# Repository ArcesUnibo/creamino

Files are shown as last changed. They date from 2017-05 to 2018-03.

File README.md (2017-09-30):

# creamino
Open-source Framework for Fast Developmnt of EEG-based BCI Systems

Download and Install git-for-windows.github.io from https://git-for-windows.github.io
Download and Install TortoiseGit from https://github.com/ArcesUnibo/creamino

To obtain creamino we would do the following:

Create a folder that will hold the Git project
example: c:\work
Selecting this folder, right click on it and use the command: Git Clone...
In the dialog we provide:
The URL of the project http://github.com/ArcesUnibo/creamino
The directory of the project. This will be automatically populated with the name of the project in our selected folder.
Select the Recursive checkbox.

Thank you for using Creamino!

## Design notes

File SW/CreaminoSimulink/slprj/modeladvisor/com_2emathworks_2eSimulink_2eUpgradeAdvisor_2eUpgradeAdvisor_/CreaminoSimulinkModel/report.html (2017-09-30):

Model Advisor Report
Simulink version: 8.4 | Model version: 1.3
System: CreaminoSimulinkModel | Current run: 10-Feb-2016 17:30:59

#### No results to display. Select one or more items in the left pane, then press Run Selected Checks.

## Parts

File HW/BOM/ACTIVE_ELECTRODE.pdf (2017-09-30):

Description | Designator | Footprint | Comment
Capacitor (Surface Mount) CP1 | CC3225-1210 220u
Capacitor (Surface Mount) CP2 | CC1005-0402 22n
Default Diode | D1 | SC79 | 1N4148
Semiconductor Resistor | R1 | CR1005-0402 1.6K
Semiconductor Resistor | R2 | CR1608-0603 71.4K
Semiconductor Resistor | R3 | CR1005-0402 604K
Semiconductor Resistor | R4 | CR1005-0402 33K
OPA378AIDBVT | U1 | SOT23-5DVB | OPA378AIDBVT

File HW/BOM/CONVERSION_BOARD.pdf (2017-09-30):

Description | Designator Footprint | Comment
ADP122-3.3 | A1 | UJ-5
ADP122-3.3 | A3 | UJ-5
ADS1298 | ADC1 | PAG64
Polarized Capacitor (Surface Mount) | CP1 | CC2012-0805 10u
Capacitor (Semiconductor SIM Model) | CP2 | CC1005-0402 100n
Capacitor (Semiconductor SIM Model) | CP3 | CC1005-0402 100n
Capacitor (Semiconductor SIM Model) | CP6 | CC1005-0402 470n
Capacitor (Semiconductor SIM Model) | CP17 | CC1005-0402 1u
Capacitor (Semiconductor SIM Model) | CP18 | CC1005-0402 1u
Capacitor (Semiconductor SIM Model) | CP25 | CC1005-0402 100n
Capacitor (Semiconductor SIM Model) | CP26 | CC1005-0402 1u
Capacitor (Semiconductor SIM Model) | CP27 | CC1005-0402 100n
Capacitor (Semiconductor SIM Model) | CP28 | CC1005-0402 1u
Capacitor (Semiconductor SIM Model) | CP29 | CC1005-0402 470n
Capacitor (Semiconductor SIM Model) | CP30 | CC1005-0402 470n
Capacitor (Semiconductor SIM Model) | CP31 | CC1005-0402 470n
Capacitor (Semiconductor SIM Model) | CP32 | CC1005-0402 470n
Capacitor (Semiconductor SIM Model) | CP33 | CC1005-0402 470n
Capacitor (Semiconductor SIM Model) | CP34 | CC1005-0402 470n
Capacitor (Semiconductor SIM Model) | CP35 | CC1005-0402 470n
Capacitor (Semiconductor SIM Model) | CP36 | CC1005-0402 470n
Polarized Capacitor (Surface Mount) | CP37 | CC1608-0603 22uF
Capacitor (Semiconductor SIM Model) | CP38 | CC1005-0402 1u
Capacitor (Semiconductor SIM Model) | CP39 | CC1005-0402 1u
Capacitor (Semiconductor SIM Model) | CP40 | CC1005-0402 100n
Capacitor (Semiconductor SIM Model) | CP41 | CC1005-0402 1u
Capacitor (Semiconductor SIM Model) | CP42 | CC1005-0402 100p
Polarized Capacitor (Surface Mount) | CP43 | CC2012-0805 10uF
Capacitor (Semiconductor SIM Model) | CP44 | CC1005-0402 100n
Capacitor (Semiconductor SIM Model) | CP45 | CC1005-0402 100n
Polarized Capacitor (Surface Mount) | CP46 | CC2012-0805 10u
Capacitor (Semiconductor SIM Model) | CP47 | CC1005-0402 100n
Polarized Capacitor (Surface Mount) | CP48 | CC2012-0805 10u
Capacitor (Semiconductor SIM Model) | CP49 | CC1005-0402 100n
Polarized Capacitor (Surface Mount) | CP50 | CC2012-0805 10u
Capacitor (Semiconductor SIM Model) | CP51 | CC1005-0402 100n
Capacitor (Semiconductor SIM Model) | CP51_TANTCC3216-1206 1u
Polarized Capacitor (Surface Mount) | CP52 | CC2012-0805 10u
Capacitor (Semiconductor SIM Model) | CP55 | CC1005-0402 1u
Capacitor (Semiconductor SIM Model) | CP56 | CC1005-0402 1u
Header, 3-Pin | JPV | HDR1X3 | JPV
ADuM2401 | O1A | RW-16
ADuM2401 | O1B | RW-16
ADUM6000 | O2 | RW-16
Header, 10-Pin, Dual row | P1 | HDR2X10 | Header 10X2
Header, 8-Pin | P3 | HDR1X8 | Dx UP
Header, 8-Pin | P4 | HDR1X8 | Dx DOWN
Header, 8-Pin | P5 | HDR1X8 | Sx UP

Header, 6-Pin | P6 | HDR1X6 | Sx DOWN
Header, 6-Pin | P7A | HDR1X6 | ADCext1
Header, 4-Pin | P7B | HDR1X4 | ADCext1
Semiconductor Resistor | R1 | CR1608-0603 8.2K
Semiconductor Resistor | R2 | CR1005-0402 56K
Semiconductor Resistor | R3 | CR1005-0402 18K
Semiconductor Resistor | R4 | CR1005-0402 33K
Semiconductor Resistor | R8 | CR1005-0402 2.2K
Semiconductor Resistor | R9 | CR1005-0402 2.2K
Semiconductor Resistor | R10 | CR1005-0402 2.2K
Semiconductor Resistor | R11 | CR1005-0402 2.2K
Semiconductor Resistor | R12 | CR1005-0402 2.2K
Semiconductor Resistor | R13 | CR1005-0402 2.2K
Semiconductor Resistor | R14 | CR1005-0402 2.2K
Semiconductor Resistor | R15 | CR1005-0402 2.2K
Semiconductor Resistor | R16 | CR1608-0603 | 220
Semiconductor Resistor | R17 | CR1608-0603 | 220
Semiconductor Resistor | R18 | CR1608-0603 | 220
Semiconductor Resistor | R19 | CR1608-0603 | 220
Semiconductor Resistor | R20 | CR1608-0603 | 220
Semiconductor Resistor | R21 | CR1608-0603 | 220
Semiconductor Resistor | R22 | CR1608-0603 | 220
Semiconductor Resistor | R23 | CR1608-0603 | 220
Semiconductor Resistor | R25 | CR1005-0402 | 0
Semiconductor Resistor | R27 | CR1005-0402 | 0
Semiconductor Resistor | R28 | CR1005-0402 10K
Semiconductor Resistor | R29 | CR1005-0402 10K
Semiconductor Resistor | R30 | CR1005-0402 10K
Semiconductor Resistor | RDAISY_IN CR1005-0402 10K
ADR433 | REF3V | RM-8
Semiconductor Resistor | RR | CR1005-0402 2.2K
OPA378AIDBVT | U2 | SOT23-5DVB

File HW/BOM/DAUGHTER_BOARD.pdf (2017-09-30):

Description | Designator Comment | Footprint
ADS1298 | ADC1 | | PAG64
Capacitor (Semiconductor SIM Model) | CP1 | 100n | CC1005-0402
Capacitor (Semiconductor SIM Model) | CP2 | 1u | CC1005-0402
Capacitor (Semiconductor SIM Model) | CP3 | 100n | CC1005-0402
Capacitor (Semiconductor SIM Model) | CP4 | 1u | CC1005-0402
Polarized Capacitor (Surface Mount) | CP5 | 22uF | CC1608-0603
Capacitor (Semiconductor SIM Model) | CP6 | 1u | CC1005-0402
Capacitor (Semiconductor SIM Model) | CP7 | 1u | CC1005-0402
Capacitor (Semiconductor SIM Model) | CP8 | 100n | CC1005-0402
Capacitor (Semiconductor SIM Model) | CP9 | 1u | CC1005-0402
Capacitor (Semiconductor SIM Model) | CP10 | 100p | CC1005-0402
Polarized Capacitor (Surface Mount) | CP11 | 10uF | CC2012-0805
Capacitor (Semiconductor SIM Model) | CP12 | 100n | CC1005-0402
Capacitor (Semiconductor SIM Model) | CP13 | 47n | CC1005-0402
Capacitor (Semiconductor SIM Model) | CP14 | 47n | CC1005-0402
Capacitor (Semiconductor SIM Model) | CP15 | 47n | CC1005-0402
Capacitor (Semiconductor SIM Model) | CP16 | 47n | CC1005-0402
Capacitor (Semiconductor SIM Model) | CP17 | 47n | CC1005-0402
Capacitor (Semiconductor SIM Model) | CP18 | 47n | CC1005-0402
Capacitor (Semiconductor SIM Model) | CP19 | 47n | CC1005-0402
Capacitor (Semiconductor SIM Model) | CP20 | 47n | CC1005-0402
Header, 8-Pin, Dual row | P1 | Header 8X2 HDR2X8
Header, 6-Pin | P2A | ADCext1 | HDR1X6
Header, 4-Pin | P2B | ADCext1 | HDR1X4
Header, 6-Pin | P3A | ADCext2 | HDR1X6
Header, 4-Pin | P3B | ADCext2 | HDR1X4
Semiconductor Resistor | R1 | 2.2K | CR1005-0402
Semiconductor Resistor | R2 | 2.2K | CR1005-0402
Semiconductor Resistor | R3 | 2.2K | CR1005-0402
Semiconductor Resistor | R4 | 2.2K | CR1005-0402
Semiconductor Resistor | R5 | 2.2K | CR1005-0402
Semiconductor Resistor | R6 | 2.2K | CR1005-0402
Semiconductor Resistor | R7 | 2.2K | CR1005-0402
Semiconductor Resistor | R8 | 2.2K | CR1005-0402
Semiconductor Resistor | R13 | | 220 CR1608-0603
Semiconductor Resistor | R14 | | 220 CR1608-0603
Semiconductor Resistor | R15 | | 220 CR1608-0603
Semiconductor Resistor | R16 | | 220 CR1608-0603
Semiconductor Resistor | R17 | | 220 CR1608-0603
Semiconductor Resistor | R18 | | 220 CR1608-0603
Semiconductor Resistor | R19 | | 220 CR1608-0603
Semiconductor Resistor | R20 | | 220 CR1608-0603
Semiconductor Resistor | RDAISY_IN 10K | CR1005-0402

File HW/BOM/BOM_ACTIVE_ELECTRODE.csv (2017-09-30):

Description | Designator | Footprint | Comment | Quantity
Capacitor (Surface Mount) | CP1 | CC3225-1210 | 220u | 1
Capacitor (Surface Mount) | CP2 | CC1005-0402 | 22n | 1
Default Diode | D1 | SC79 | 1N4148 | 1
Semiconductor Resistor | R1 | CR1005-0402 | 1.6K | 1
Semiconductor Resistor | R2 | CR1608-0603 | 71.4K | 1
Semiconductor Resistor | R3 | CR1005-0402 | 604K | 1
Semiconductor Resistor | R4 | CR1005-0402 | 33K | 1
OPA378AIDBVT | U1 | SOT23-5DVB | OPA378AIDBVT | 1

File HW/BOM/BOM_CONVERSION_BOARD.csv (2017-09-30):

Description | Designator | Footprint | Comment | Quantity
ADP122-3.3 | A1 | UJ-5 |  | 1
ADP122-3.3 | A3 | UJ-5 |  | 1
ADS1298 | ADC1 | PAG64 |  | 1
Polarized Capacitor (Surface Mount) | CP1 | CC2012-0805 | 10u | 1
Capacitor (Semiconductor SIM Model) | CP2 | CC1005-0402 | 100n | 1
Capacitor (Semiconductor SIM Model) | CP3 | CC1005-0402 | 100n | 1
Capacitor (Semiconductor SIM Model) | CP6 | CC1005-0402 | 470n | 1
Capacitor (Semiconductor SIM Model) | CP17 | CC1005-0402 | 1u | 1
Capacitor (Semiconductor SIM Model) | CP18 | CC1005-0402 | 1u | 1
Capacitor (Semiconductor SIM Model) | CP25 | CC1005-0402 | 100n | 1
Capacitor (Semiconductor SIM Model) | CP26 | CC1005-0402 | 1u | 1
Capacitor (Semiconductor SIM Model) | CP27 | CC1005-0402 | 100n | 1
Capacitor (Semiconductor SIM Model) | CP28 | CC1005-0402 | 1u | 1
Capacitor (Semiconductor SIM Model) | CP29 | CC1005-0402 | 470n | 1
Capacitor (Semiconductor SIM Model) | CP30 | CC1005-0402 | 470n | 1
Capacitor (Semiconductor SIM Model) | CP31 | CC1005-0402 | 470n | 1
Capacitor (Semiconductor SIM Model) | CP32 | CC1005-0402 | 470n | 1
Capacitor (Semiconductor SIM Model) | CP33 | CC1005-0402 | 470n | 1
Capacitor (Semiconductor SIM Model) | CP34 | CC1005-0402 | 470n | 1
Capacitor (Semiconductor SIM Model) | CP35 | CC1005-0402 | 470n | 1
Capacitor (Semiconductor SIM Model) | CP36 | CC1005-0402 | 470n | 1
Polarized Capacitor (Surface Mount) | CP37 | CC1608-0603 | 22uF | 1
Capacitor (Semiconductor SIM Model) | CP38 | CC1005-0402 | 1u | 1
Capacitor (Semiconductor SIM Model) | CP39 | CC1005-0402 | 1u | 1
Capacitor (Semiconductor SIM Model) | CP40 | CC1005-0402 | 100n | 1
Capacitor (Semiconductor SIM Model) | CP41 | CC1005-0402 | 1u | 1
Capacitor (Semiconductor SIM Model) | CP42 | CC1005-0402 | 100p | 1
Polarized Capacitor (Surface Mount) | CP43 | CC2012-0805 | 10uF | 1
Capacitor (Semiconductor SIM Model) | CP44 | CC1005-0402 | 100n | 1
Capacitor (Semiconductor SIM Model) | CP45 | CC1005-0402 | 100n | 1
Polarized Capacitor (Surface Mount) | CP46 | CC2012-0805 | 10u | 1
Capacitor (Semiconductor SIM Model) | CP47 | CC1005-0402 | 100n | 1
Polarized Capacitor (Surface Mount) | CP48 | CC2012-0805 | 10u | 1
Capacitor (Semiconductor SIM Model) | CP49 | CC1005-0402 | 100n | 1
Polarized Capacitor (Surface Mount) | CP50 | CC2012-0805 | 10u | 1
Capacitor (Semiconductor SIM Model) | CP51 | CC1005-0402 | 100n | 1
Capacitor (Semiconductor SIM Model) | CP51_TANT | CC3216-1206 | 1u | 1
Polarized Capacitor (Surface Mount) | CP52 | CC2012-0805 | 10u | 1
Capacitor (Semiconductor SIM Model) | CP55 | CC1005-0402 | 1u | 1
Capacitor (Semiconductor SIM Model) | CP56 | CC1005-0402 | 1u | 1
Header, 3-Pin | JPV | HDR1X3 | JPV | 1
ADuM2401 | O1A | RW-16 |  | 1
ADuM2401 | O1B | RW-16 |  | 1
ADUM6000 | O2 | RW-16 |  | 1
Header, 10-Pin, Dual row | P1 | HDR2X10 | Header 10X2 | 1
Header, 8-Pin | P3 | HDR1X8 | Dx UP | 1
Header, 8-Pin | P4 | HDR1X8 | Dx DOWN | 1
Header, 8-Pin | P5 | HDR1X8 | Sx UP | 1
Header, 6-Pin | P6 | HDR1X6 | Sx DOWN | 1
Header, 6-Pin | P7A | HDR1X6 | ADCext1 | 1
Header, 4-Pin | P7B | HDR1X4 | ADCext1 | 1
Semiconductor Resistor | R1 | CR1608-0603 | 8.2K | 1
Semiconductor Resistor | R2 | CR1005-0402 | 56K | 1
Semiconductor Resistor | R3 | CR1005-0402 | 18K | 1
Semiconductor Resistor | R4 | CR1005-0402 | 33K | 1
Semiconductor Resistor | R8 | CR1005-0402 | 2.2K | 1
Semiconductor Resistor | R9 | CR1005-0402 | 2.2K | 1
Semiconductor Resistor | R10 | CR1005-0402 | 2.2K | 1
Semiconductor Resistor | R11 | CR1005-0402 | 2.2K | 1
Semiconductor Resistor | R12 | CR1005-0402 | 2.2K | 1
Semiconductor Resistor | R13 | CR1005-0402 | 2.2K | 1
Semiconductor Resistor | R14 | CR1005-0402 | 2.2K | 1
Semiconductor Resistor | R15 | CR1005-0402 | 2.2K | 1
Semiconductor Resistor | R16 | CR1608-0603 | 220 | 1
Semiconductor Resistor | R17 | CR1608-0603 | 220 | 1
Semiconductor Resistor | R18 | CR1608-0603 | 220 | 1
Semiconductor Resistor | R19 | CR1608-0603 | 220 | 1
Semiconductor Resistor | R20 | CR1608-0603 | 220 | 1
Semiconductor Resistor | R21 | CR1608-0603 | 220 | 1
Semiconductor Resistor | R22 | CR1608-0603 | 220 | 1
Semiconductor Resistor | R23 | CR1608-0603 | 220 | 1
Semiconductor Resistor | R25 | CR1005-0402 | 0 | 1
Semiconductor Resistor | R27 | CR1005-0402 | 0 | 1
Semiconductor Resistor | R28 | CR1005-0402 | 10K | 1
Semiconductor Resistor | R29 | CR1005-0402 | 10K | 1
Semiconductor Resistor | R30 | CR1005-0402 | 10K | 1
Semiconductor Resistor | RDAISY_IN | CR1005-0402 | 10K | 1
ADR433 | REF3V | RM-8 |  | 1
Semiconductor Resistor | RR | CR1005-0402 | 2.2K | 1
OPA378AIDBVT | U2 | SOT23-5DVB |  | 1

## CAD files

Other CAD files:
SW/CreaminoSimulink/slprj/_sfprj/CreaminoSimulinkModel/_self/sfun/src/c2_creaminosimulinkmodel.obj
SW/CreaminoSimulink/slprj/_sfprj/untitled/_self/sfun/src/untitled_sfun_registry.obj
SW/CreaminoSimulink/slprj/_sfprj/CreaminoSimulinkModel/_self/sfun/src/creaminosimulinkmodel_sfun.obj
SW/CreaminoSimulink/slprj/_sfprj/untitled/_self/sfun/src/c2_untitled.obj
SW/CreaminoSimulink/slprj/_sfprj/CreaminoSimulinkModel/_self/sfun/src/creaminosimulinkmodel_sfun_registry.obj
SW/CreaminoSimulink/slprj/_sfprj/untitled/_self/sfun/src/untitled_sfun.obj
SW/CreaminoSimulink/slprj/_sfprj/CreaminoSimulinkModel/_self/sfun/src/lccstub.obj
SW/CreaminoSimulink/slprj/_sfprj/untitled/_self/sfun/src/lccstub.obj

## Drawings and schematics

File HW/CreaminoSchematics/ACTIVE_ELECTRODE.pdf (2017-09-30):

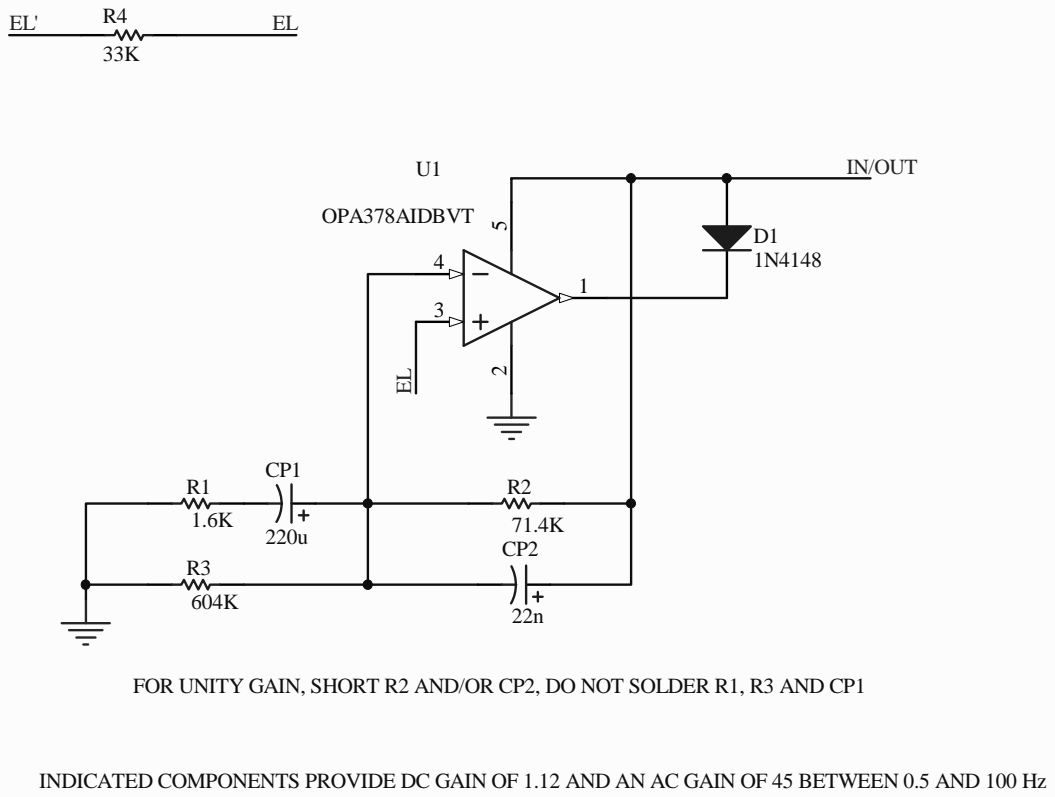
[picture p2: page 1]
Title; Size; Number; Revision; Date:; Sheet of; File:; \\..\ElettrodoPreAmp3_3.SCHDOC; Drawn By:; IN/OUT; OPA378AIDBVT; CREAMINO - ACTIVE ELECTRODE

FOR UNITY GAIN, SHORT R2 AND/OR CP2, DO NOT SOLDER R1, R3 AND CP1

INDICATED COMPONENTS PROVIDE DC GAIN OF 1.12 AND AN AC GAIN OF 45 BETWEEN 0.5 AND 100 Hz

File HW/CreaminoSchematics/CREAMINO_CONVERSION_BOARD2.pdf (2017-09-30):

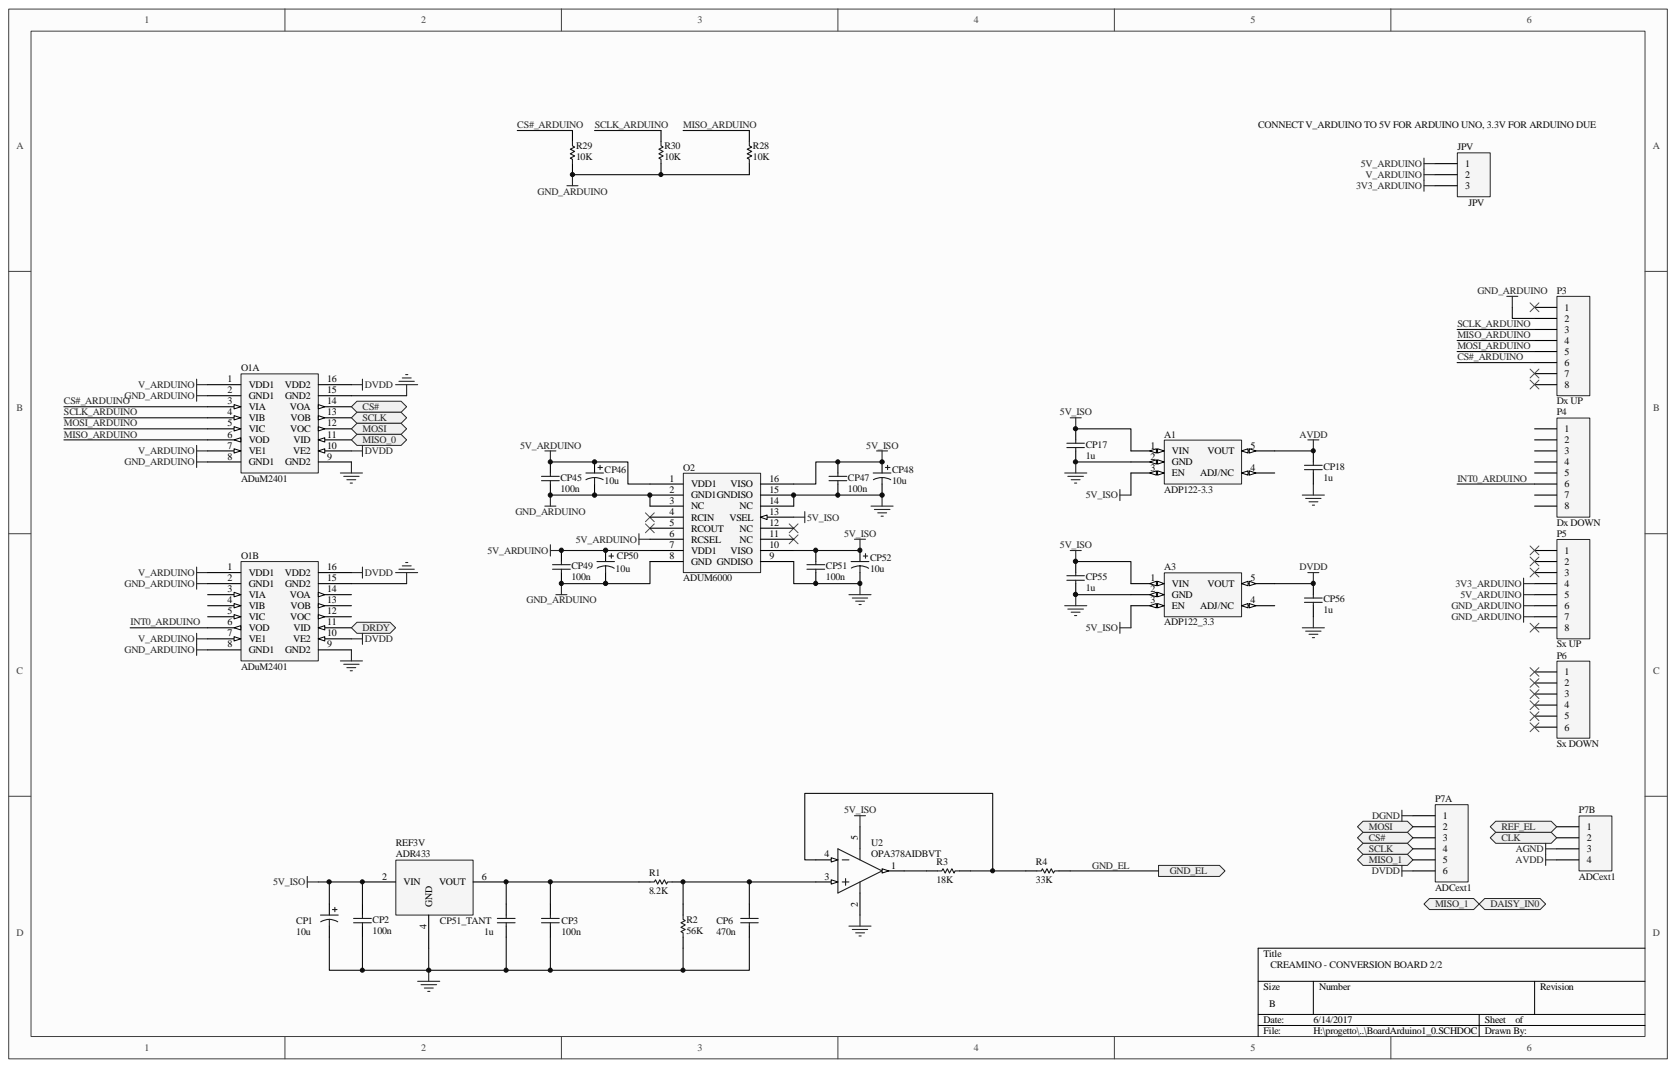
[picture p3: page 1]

CONNECT V_ARDUINO TO 5V FOR ARDUINO UNO, 3.3V FOR ARDUINO DUE

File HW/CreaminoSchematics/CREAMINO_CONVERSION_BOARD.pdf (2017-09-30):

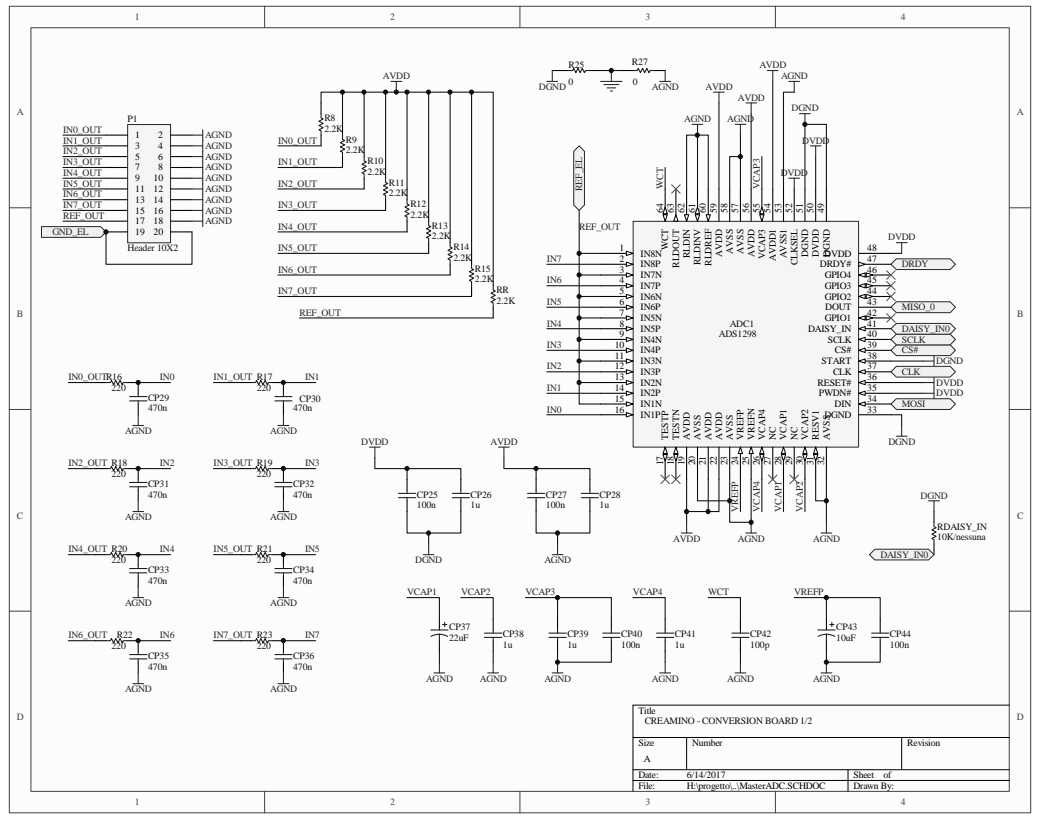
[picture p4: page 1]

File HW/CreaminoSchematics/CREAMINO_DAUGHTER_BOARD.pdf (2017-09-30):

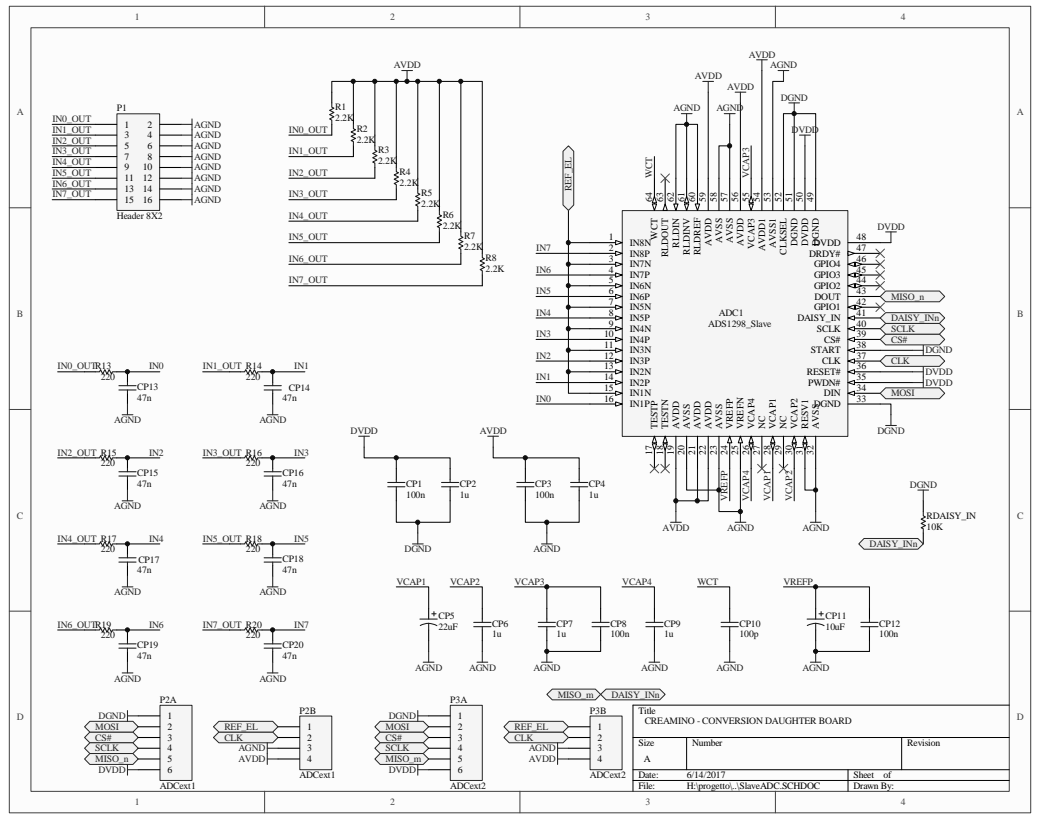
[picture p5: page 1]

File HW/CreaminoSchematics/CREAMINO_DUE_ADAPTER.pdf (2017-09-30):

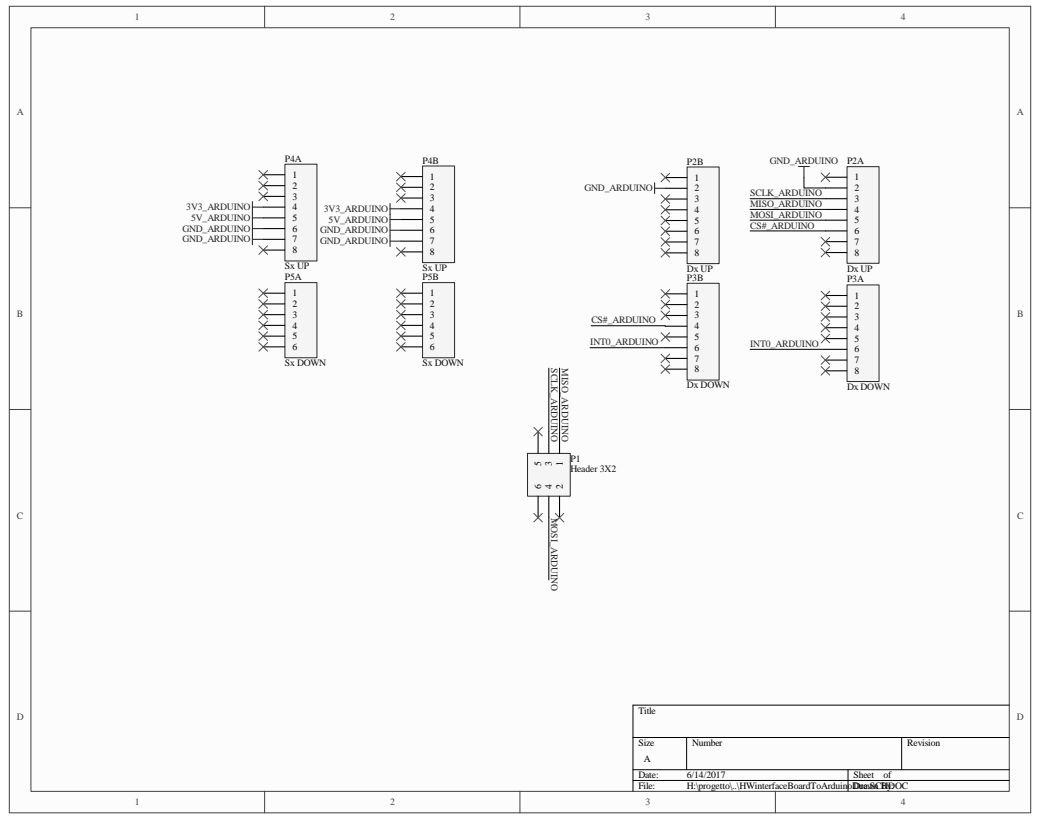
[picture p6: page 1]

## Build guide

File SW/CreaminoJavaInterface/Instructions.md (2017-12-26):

1) How to use the Java Interface

In order to use the Java Interface you go on creamino\SW\CreaminoJavaInterface\dist 
Then double click on CreaminoJavaInterface.jar file. The interface appears.
Connect the Arduino Native port to a PC USB then click on the search button on the left under COM ports.
This perform a check on the available COM port. Chose the right one. 
(For further information on Arduino COM ports do on: https://www.arduino.cc/en/Guide/ArduinoDue) 
Once this has been done configure your EEG system. The ADS model (in our case ADS1298) the chip select (4),
the sample rate (500 SPS) the number of ADC Channels, the scale, the filter type and the gain for each channel.
In addition you can chose between the ADS mode. This allows you to configure the board in normal mode to acquire
EEG signals or to use the autogenerate test signals from the ADS1298.
For further information on how to configure ADS1298 please read http://www.ti.com/product/ADS1298 

2) How to modify the Java Interface as you want

In order to modify the interface you have to download Netbeans from here:
https://netbeans.org/downloads/

a) Download and Install Netbeans IDE from here : https://netbeans.org/downloads/
 
b) Open the Netbeans IDE 
Click on File-> Open project and then select CreaminoJavaInterface located in the SW folder of the repository.
If you chose to put the repository in the directory C:\WORK is simple

Otherwise you get two errors that you need to solve.
In order to resolve errors you need to download and import two libraries.
The first one is jssc available at https://github.com/scream3r/java-simple-serial-connector/releases.
Download the jSSC-2.8.0-Release.zip and unpacket the archieve using winzip or 7-zip
Then on Netbeans select Tools->Libraries
Add the jssc-2.8.0 libraries by including the Classpath the Sources and the Javadoc that you found in the jSSC-2.8.0-Release.zip
The same must be done with the aqua libraries available here: http://aquafx-project.com/downloads.html

c) Modify the interface

From the Netbeans IDE knowing a bit of Java you can modify the interface as you want.

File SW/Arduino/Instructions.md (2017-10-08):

In order to program the Arduino Board you have to follow these instructions.

1) Install the Arduino Desktop IDE

Instructions are available at https://www.arduino.cc/en/Guide/HomePage

2) Installing Additional Arduino Cores

Only AVR Arduino boards are installed by default. 
Some Arduino boards require an additional Core to be installed (e.g. the Arduino Due used in this work)
In order for the Arduino IDE to be able to program an Arduino Due, you need to install the SAM Core 
using the Boards Manager. Instructions are reported here: https://www.arduino.cc/en/Guide/Cores

3) Copy the sketch and the library

Copy the Arduino sketch ADS1298_ArduinoDue in the folder
/Users/<username>/Documents/Arduino/ADS1298_ArduinoDue/
Be aware that the name of the sketch and the name of the last folder must be the same. So if you decide
to rename the sketch you have to do the same with the last folder

Copy the library folder in:
/Users/<username>/Documents/Arduino/libraries/

4) Upload the software on Arduino

Connect your Arduino DUE programming port to your PC or MAC via USB
Before uploading your sketch, you need to select the correct items from the Tools > Board and Tools > Port menus. 
Once you've selected the correct serial port and board, press the upload button in the toolbar or select the Upload item from the Sketch menu. 
Current Arduino boards will reset automatically and begin the upload. You'll see the RX and TX LEDs blink as the sketch is uploaded. 
The Arduino Software (IDE) will display a message when the upload is complete.
For further information follows the instructions reported here: https://www.arduino.cc/en/Guide/Environment#toc9

5) Usege of Creamino
Attach the shield to the Arduino board. Use the Native port to acquire EEG signals and the Programming port to send the trigger.

For further information refer to the paper which describes several setup experiments.

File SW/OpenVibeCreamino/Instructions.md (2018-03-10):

1) Download and Compile OpenVIbE on Windows

Download a stable source code of OpenViBE from here: http://openvibe.inria.fr/downloads/

Before to build OpenVibe download and install Phyton3 from here: https://www.python.org/downloads/ 
Once you have installed python open a cmd prompt as administrator and install jinja2 in this way:
type "c:\python3X\Scripts\pip.exe install jinja2" (Check if the installation path of python is correct, 
otherwise modify the path)

Use the same cmd prompt and go inside the OpenViBE folder than run install_dependencies.cmd

Be sure to have gtk library installed. If not Download MSYS2 installer from here: http://www.msys2.org/
Download and install the version that matchs your platform. Open the MSYS2 shell and type: pacman -S mingw-w64-x86_64-gtk3

Be sure to have Microsoft Visual Studio 2013 installed.
Once the dependencies have been installed you can run the build.cmd --vsbuild-all if you intend to use Visual Studio as we did.

For further details follow the instructions reported here : http://openvibe.inria.fr/build-instructions/

2) Put the acquisition driver inside OpenVIbE

Put the source files that you can find in C:/WORK/creamino/SW/OpenVibeCreamino/creamino/src
in your local repository:
[openvibe-repository]/contrib/plugins/server-drivers/creamino/src/ 

Put the glade interface that you can find in C:/WORK/creamino/SW/OpenVibeCreamino/creamino/share interface-Creamino.glade in your local repository:
[openvibe-repository]/contrib/plugins/server-drivers/[my-device]/share/

Don't forget to declare your driver to the Acquisition Server application.
This happens in "./contrib/common/contribAcquisitionServer.inl". There you 
will find examples of such declarations. You also need to register the source
files to CMake, modifying the corresponding "contribAcquisitionServer.cmake".

For more information about building a new driver and filling your skeleton, please read the official tutorial:
http://openvibe.inria.fr/tutorial-creating-a-new-driver-for-the-acquisition-server/

Run once again the command build.cmd --vsbuild-all

Put the file Calibration.csv inside the folder [openvibe-repository]/dist/extras/Release

You are ready to use Creamino inside OpenViBE!

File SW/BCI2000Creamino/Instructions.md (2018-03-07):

1) Download and Compile BCI2000 on Windows

Detailed instructions can be found here: https://www.bci2000.org/mediawiki/index.php/Programming_Reference:BCI2000_Source_Code
The BCI2000 source code is managed with the help of Subversion, an open-source cross-platform versioning tool widely used in various kinds of projects.
We suggest you to use TortoiseSVN, a comfortable-to-use SVN client integrated into the Explorer shell
Tortoise SVN can be downloaded here https://tortoisesvn.net/downloads.html
Access to the BCI2000 source code requires a BCI2000 user account, and agreeing to the GNU Public License (GPL). 
You may create a user account online, as described on the "Creating a User Account" page. https://www.bci2000.org/mediawiki/index.php/User_Accounts

If TortoiseSVN gives you an error like this "Error running context: An error occurred during authentication" during the download follow these steps:

1. Start | Control Panel | Credential Manager, 

2. Click 'Add a Windows Credential', 

3. As 'Internet or network address' enter the FQDN of VisualSVN Server's machine, 

4. As 'Username' enter the <DOMAIN>\<username> of user account that exists in domain and has access rights to VisualSVN Server, 

Complete the password field and click OK. 
Verify that you can authenticate to VisualSVN Server under the selected user account after completing the above steps. 

In order to Compile BCI2000 follow the instruction reported here:
https://www.bci2000.org/mediawiki/index.php/Programming_Reference:Build_System

2) Put the acquisition driver inside BCI2000

In order to put the acquisition driver inside BCI2000 run the executable NewBCI2000Module that you can find inside the folder [BCI2000-repository]\BCI2000\build
and follow these instructions:

Enter module type [default is 2]: 1
Enter module name: Creamino
Enter parent directory [recommended default is "src/custom" ]: src/custom

A new SignalSource project has been created at src/custom/creamino
-- created src/custom/creamino/CMakeLists.txt
Adding filter CreaminoADC to module src/custom/creamino/
-- created src/custom/creamino/CreaminoADC.cpp
-- created src/custom/creamino/CreaminoADC.h
-- added CreaminoADC.cpp to src/custom/creamino/CMakeLists.txt

Put the source files that you can find in C:/WORK/creamino/SW/BCI2000/creamino/src
in your local repository:
[BCI2000-repository]/src/custom/creamino/ 

Put the Calibration file (Calibration.csv) that you can find in C:/WORK/creamino/SW/BCI2000/creamino/src
in your local repository:
[BCI2000-repository]/prog 

NOTE: Run CMake again to ensure that this module is included in the build.

To expand the new module, edit the following files:
* src/custom/creamino/Creamino/CMakeLists.txt	
* src/custom/creamino/Creamino/CreaminoADC.cpp
* src/custom/creamino/Creamino/CreaminoADC.h

You are ready to use Creamino inside BCI2000!

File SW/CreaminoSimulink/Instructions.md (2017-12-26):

1) How to use Creamino in Simulink

In order to import signals coming from Creamino directly into Simulink you need a Simulink licence.
If you have already installed Simulink on your PC double click on CreaminoSimulinkModel in the folder C:\WORK\creamino\SW\CreaminoSimulink 
This automatically open Matlab and Simulink 
Double click on the Creamino block to set the correct parameters. Modify the field parameters.
You have to set:
The COM port
The ADS type
The sample rate
The gain of the ADS channels
Test or Normal mode
The number of channels
The input buffer size.

Example:
'COM17','ADS1298','500SPS',1,'Test',8,8

Connect the Arduino Native port to a USB.
Then run the Simulink Model. You can add all the Simulink blocks needed to perform your signal process.
For further information on how to Use Creamino Inside Simulink watch the video available in this folder.

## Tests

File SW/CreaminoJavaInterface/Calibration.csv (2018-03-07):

CH1 | 2.0
CH2 | 1.0
CH3 | 1.0
CH4 | 1.0
CH5 | 1.0
CH6 | 1.0
CH7 | 1.0
CH8 | 1.0
CH9 | 1.0
CH10 | 1.0
CH11 | 1.0
CH12 | 1.0
CH13 | 1.0
CH14 | 1.0
CH15 | 1.0
CH16 | 1.0
CH17 | 1.0
CH18 | 1.0
CH19 | 1.0
CH20 | 1.0
CH21 | 1.0
CH22 | 1.0
CH23 | 1.0
CH24 | 1.0
CH25 | 1.0
CH26 | 1.0
CH27 | 1.0
CH28 | 1.0
CH29 | 1.0
CH30 | 1.0
CH31 | 1.0
CH32 | 1.0
CH33 | 1.0
CH34 | 1.0
CH35 | 1.0
CH36 | 1.0
CH37 | 1.0
CH38 | 1.0
CH39 | 1.0
CH40 | 1.0
CH41 | 1.0
CH42 | 1.0
CH43 | 1.0
CH44 | 1.0
CH45 | 1.0
CH46 | 1.0
CH47 | 1.0
CH48 | 1.0
CH49 | 1.0
CH50 | 1.0
CH51 | 1.0
CH52 | 1.0
CH53 | 1.0
CH54 | 1.0
CH55 | 1.0
CH56 | 1.0
CH57 | 1.0
CH58 | 1.0
CH59 | 1.0
CH60 | 1.0
CH61 | 1.0
CH62 | 1.0
CH63 | 1.0
CH64 | 1.0

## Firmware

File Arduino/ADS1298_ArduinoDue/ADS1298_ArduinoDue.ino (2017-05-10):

// include the libraries:

#include <SPI.h>
#include "ADS1298.h" //find all definition for ADS1298

//Type
ADS1298 ADS1298device;

// global variable
int transmit = 0;
volatile int interrupt_pin2 = 0;
int connect;
byte SampleRate[1];
byte ModeADS[1];
byte ADSNum[1];
byte ChipSelect[1];
byte TriggerWord[1];
byte Gain[1];

boolean toggle = 0;
String ConnectingWord;

void setup() {

  //prova
  ModeADS[0] = 0x00;
  ADSNum[0] = 0x00;
  
  connect=0;  //Disconnect from a user Interface (Java, C++)  
  attachInterrupt(2, SPIInterrupt, FALLING); //Interrupt on ArduinoDue // 2 menas pin 2
  
  Serial.begin(9600); //USB programming port Init --> for trigger
  Serial.flush();
  
  SerialUSB.begin(256000);  // USB Initialization
  SerialUSB.flush();
  delay(100);

  pinMode(13, OUTPUT); // LED pin for debug
  digitalWrite(13, toggle);
  TriggerWord[0] = 0x00;  
}


//interrupt function IR2
void SPIInterrupt() {
    interrupt_pin2 = 1;
}

void loop() {

  //Arduino Connection and ADC initialization
  while(!connect){
    if(SerialUSB.available()>6){ // Check if data are available on the serial bus
      ConnectingWord = SerialUSB.readString(); //Read data
      if(ConnectingWord.equals("Connect")){ //Check the connecting word
        connect = 1;
        SerialUSB.println("Ready"); // Send the ack word //println-->write
        delay(500);
        
        while(!SerialUSB.available()>3); // Wait the Sample Rate
         
        SerialUSB.readBytes(SampleRate,1);  //Read the sample rate;
        SerialUSB.readBytes(ModeADS,1);  //Read the Mode;
        SerialUSB.readBytes(ADSNum,1);  //Read the number of ADS;
        SerialUSB.readBytes(ChipSelect,1);  //Read the Chip Select;
        SerialUSB.readBytes(Gain,1);  //Read the Chip Select;
        
        delay(100);
  
        ADS1298device.initialize(SampleRate[0],ADSNum[0],ChipSelect[0]); //Initialize the ADS
        delay(100);

        ADS1298device.reINITforMoreADC(SampleRate[0], ModeADS[0]); //Configure the ADS channels
        delay(100); 
 
        ADS1298device.START(); //Start conversion
        delay(100);

         if (Serial.available() > 0) //Flush the Trigger buffer
           Serial.read();

        toggle = !toggle;
        digitalWrite(13, toggle);
      }  
    } 
  }

  //ADC Acquisition
  
  if(interrupt_pin2==1){
    ADS1298device.RDATA();
    ADS1298device.writeADSchannelData(TriggerWord[0]);
    interrupt_pin2 = 0;  
    TriggerWord[0] = 0x00;
  }
  
  //Arduino Connection and ADC initialization
  
  if(connect){
    if(SerialUSB.available()>9){
      ConnectingWord = SerialUSB.readStringUntil('\0');
      
      if(ConnectingWord.equals("Disconnect")){
        toggle = !toggle;
        digitalWrite(13, toggle);
        connect = 0;
        ADS1298device.STOP();
        delay(100);
        SerialUSB.flush();
      }
    }
    
    if(Serial.available()){
      Serial.readBytes(TriggerWord,1);
      Serial.println(TriggerWord[0]);
    }    
  }
}

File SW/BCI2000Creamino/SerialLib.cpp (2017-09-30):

/*Matteo Chiesi - University of Bologna*/
//SerialLib.cpp

#include "SerialLib.h"
#include <vector>
using namespace std;

namespace SerialLibrary
{

	/*
	* Get serial port names
	*/

	std::vector<std::string> SerialLib::getSerialPortNames()
	{

		HKEY phkResult;
		LPCWSTR lpSubKey = (LPCWSTR)"HARDWARE\\DEVICEMAP\\SERIALCOMM\\";
		std::vector<std::string>  returnArray;

		if (RegOpenKeyExA(HKEY_LOCAL_MACHINE, (LPCSTR)lpSubKey, 0, KEY_READ, &phkResult) == ERROR_SUCCESS) {
			bool hasMoreElements = true;
			DWORD keysCount = 0;
			char valueName[256];
			DWORD valueNameSize;
			DWORD enumResult;
			while (hasMoreElements) {
				valueNameSize = 256;
				enumResult = RegEnumValueA(phkResult, keysCount, valueName, &valueNameSize, NULL, NULL, NULL, NULL);
				if (enumResult == ERROR_SUCCESS) {
					keysCount++;
				}
				else if (enumResult == ERROR_NO_MORE_ITEMS) {
					hasMoreElements = false;
				}
				else {
					hasMoreElements = false;
				}
			}
			if (keysCount > 0) {
				returnArray.resize(keysCount);

				char lpValueName[256];
				DWORD lpcchValueName;
				byte lpData[256];
				DWORD lpcbData;
				DWORD result;
				for (DWORD i = 0; i < keysCount; i++) {
					lpcchValueName = 256;
					lpcbData = 256;
					result = RegEnumValueA(phkResult, i, lpValueName, &lpcchValueName, NULL, NULL, lpData, &lpcbData);
					if (result == ERROR_SUCCESS) {
						returnArray[i].append((char*)lpData);
					}
				}
			}
			CloseHandle(phkResult);
		}
		return returnArray;
	}


	/*
	* Port opening.
	*
	* In 2.2.0 added useTIOCEXCL (not used in Windows, only for compatibility with _nix version)
	*/
	HANDLE SerialLib::openPort(string portName, bool useTIOCEXCL) {

		string prefix = "\\\\.\\";
		string portFullName = prefix + portName;

		std::string stemp = std::string(portFullName.begin(), portFullName.end());
		LPCSTR swportFullName = stemp.c_str();

		HANDLE hComm = CreateFile(swportFullName,
			GENERIC_READ | GENERIC_WRITE, //access ( read and write)
			0, //(share) 0:cannot share the COM port
			0, //security  (None) 
			OPEN_EXISTING, // creation : open_existing
			FILE_FLAG_OVERLAPPED,  // we dont want overlapped operation
			0); // no templates file for COM port...

				//since 2.3.0 ->
		if (hComm != INVALID_HANDLE_VALUE) {
			DCB *dcb = new DCB();
			if (!GetCommState(hComm, dcb)) {
				CloseHandle(hComm);//since 2.7.0
				hComm = (HANDLE)ERR_INCORRECT_SERIAL_PORT;//(-4)Incorrect serial port
			}
			delete dcb;
		}
		else {
			DWORD errorValue = GetLastError();
			if (errorValue == ERROR_ACCESS_DENIED) {
				hComm = (HANDLE)ERR_PORT_BUSY;//(-1)Port busy
			}
			else if (errorValue == ERROR_FILE_NOT_FOUND) {
				hComm = (HANDLE)ERR_PORT_NOT_FOUND;//(-2)Port not found
			}
		}
		//<- since 2.3.0
		return hComm;//since 2.4.0 changed to jlong
	};


	/*
	* Setting serial port params.
	*
	* In 2.6.0 added flags (not used in Windows, only for compatibility with _nix version)
	*/
	bool SerialLib::setParams(HANDLE portHandle, int baudRate, int byteSize, int stopBits, int parity, bool setRTS, bool setDTR, int flags) {
		HANDLE hComm = (HANDLE)portHandle;
		DCB *dcb = new DCB();
		bool returnValue = false;
		if (GetCommState(hComm, dcb)) {
			dcb->BaudRate = baudRate;
			dcb->ByteSize = byteSize;
			dcb->StopBits = stopBits;
			dcb->Parity = parity;

			//since 0.8 ->
			if (setRTS == true) {
				dcb->fRtsControl = RTS_CONTROL_ENABLE;
			}
			else {
				dcb->fRtsControl = RTS_CONTROL_DISABLE;
			}
			if (setDTR == false) {
				dcb->fDtrControl = DTR_CONTROL_ENABLE;
			}
			else {
				dcb->fDtrControl = DTR_CONTROL_DISABLE;
			}
			dcb->fOutxCtsFlow = FALSE;
			dcb->fOutxDsrFlow = FALSE;
			dcb->fDsrSensitivity = FALSE;
			dcb->fTXContinueOnXoff = TRUE;
			dcb->fOutX = FALSE;
			dcb->fInX = FALSE;
			dcb->fErrorChar = FALSE;
			dcb->fNull = FALSE;
			dcb->fAbortOnError = FALSE;
			dcb->XonLim = 2048;
			dcb->XoffLim = 512;
			dcb->XonChar = (char)17; //DC1
			dcb->XoffChar = (char)19; //DC3
									  //<- since 0.8

			if (SetCommState(hComm, dcb)) {

				//since 2.1.0 -> previously setted timeouts by another application should be cleared
				COMMTIMEOUTS *lpCommTimeouts = new COMMTIMEOUTS();
				lpCommTimeouts->ReadIntervalTimeout = 0;
				lpCommTimeouts->ReadTotalTimeoutConstant = 0;
				lpCommTimeouts->ReadTotalTimeoutMultiplier = 0;
				lpCommTimeouts->WriteTotalTimeoutConstant = 0;
				lpCommTimeouts->WriteTotalTimeoutMultiplier = 0;
				if (SetCommTimeouts(hComm, lpCommTimeouts)) {
					returnValue = true;
				}
				delete lpCommTimeouts;
				//<- since 2.1.0
			}
		}
		delete dcb;
		return returnValue;
	}

	/*
	* PurgeComm
	*/
	bool SerialLib::purgePort(HANDLE portHandle, int flags) {
		HANDLE hComm = (HANDLE)portHandle;
		DWORD dwFlags = (DWORD)flags;
		return (PurgeComm(hComm, dwFlags) ? true : false);
	}

	/*
	* Port closing
	*/
	bool  SerialLib::closePort(HANDLE portHandle) {
		HANDLE hComm = (HANDLE)portHandle;
		return (CloseHandle(hComm) ? true : false);
	}

	/*
	* Set events mask
	*/
	bool SerialLib::setEventsMask(HANDLE portHandle, int mask) {
		HANDLE hComm = (HANDLE)portHandle;
		DWORD dwEvtMask = (DWORD)mask;
		return (SetCommMask(hComm, dwEvtMask) ? true : false);
	}



	/*
	* Get events mask
	*/
	int  SerialLib::getEventsMask(HANDLE portHandle) {
		HANDLE hComm = (HANDLE)portHandle;
		DWORD lpEvtMask;
		if (GetCommMask(hComm, &lpEvtMask)) {
			return (int)lpEvtMask;
		}
		else {
			return -1;
		}
	}

	/*
	* Change RTS line state (ON || OFF)
	*/
	bool SerialLib::setRTS(HANDLE portHandle, bool enabled) {
		HANDLE hComm = (HANDLE)portHandle;
		if (enabled == true) {
			return (EscapeCommFunction(hComm, SETRTS) ? true : false);
		}
		else {
			return (EscapeCommFunction(hComm, CLRRTS) ? true : false);
		}
	}

	/*
	* Change DTR line state (ON || OFF)
	*/
	bool SerialLib::setDTR(HANDLE portHandle, bool enabled) {
		HANDLE hComm = (HANDLE)portHandle;
		if (enabled == true) {
			return (EscapeCommFunction(hComm, SETDTR) ? true : false);
		}
		else {
			return (EscapeCommFunction(hComm, CLRDTR) ? true : false);
		}
	}

	/*
	* Wait event
	* portHandle - port handle
	*/
	vector<int> SerialLib::waitEvents(HANDLE portHandle) {
		HANDLE hComm = (HANDLE)portHandle;
		DWORD lpEvtMask = 0;
		DWORD lpNumberOfBytesTransferred = 0;
		OVERLAPPED *overlapped = new OVERLAPPED();
		vector<int>  returnValues(2);
		bool functionSuccessful = false;
		overlapped->hEvent = CreateEventA(NULL, true, false, NULL);
		if (WaitCommEvent(hComm, &lpEvtMask, overlapped)) {
			functionSuccessful = true;
		}
		else if (GetLastError() == ERROR_IO_PENDING) {
			if (WaitForSingleObject(overlapped->hEvent, INFINITE) == WAIT_OBJECT_0) {
				if (GetOverlappedResult(hComm, overlapped, &lpNumberOfBytesTransferred, false)) {
					functionSuccessful = true;
				}
			}
		}
		if (functionSuccessful) {
			bool executeGetCommModemStatus = false;
			bool executeClearCommError = false;
			DWORD events[9];//fixed since 0.8 (old value is 8)
			int eventsCount = 0;
			if ((EV_BREAK & lpEvtMask) == EV_BREAK) {
				events[eventsCount] = EV_BREAK;
				eventsCount++;
			}
			if ((EV_CTS & lpEvtMask) == EV_CTS) {
				events[eventsCount] = EV_CTS;
				eventsCount++;
				executeGetCommModemStatus = true;
			}
			if ((EV_DSR & lpEvtMask) == EV_DSR) {
				events[eventsCount] = EV_DSR;
				eventsCount++;
				executeGetCommModemStatus = true;
			}
			if ((EV_ERR & lpEvtMask) == EV_ERR) {
				events[eventsCount] = EV_ERR;
				eventsCount++;
				executeClearCommError = true;
			}
			if ((EV_RING & lpEvtMask) == EV_RING) {
				events[eventsCount] = EV_RING;
				eventsCount++;
				executeGetCommModemStatus = true;
			}
			if ((EV_RLSD & lpEvtMask) == EV_RLSD) {
				events[eventsCount] = EV_RLSD;
				eventsCount++;
				executeGetCommModemStatus = true;
			}
			if ((EV_RXCHAR & lpEvtMask) == EV_RXCHAR) {
				events[eventsCount] = EV_RXCHAR;
				eventsCount++;
				executeClearCommError = true;
			}
			if ((EV_RXFLAG & lpEvtMask) == EV_RXFLAG) {
				events[eventsCount] = EV_RXFLAG;
				eventsCount++;
				executeClearCommError = true;
			}
			if ((EV_TXEMPTY & lpEvtMask) == EV_TXEMPTY) {
				events[eventsCount] = EV_TXEMPTY;
				eventsCount++;
				executeClearCommError = true;
			}
			/*
			* Execute GetCommModemStatus function if it's needed (get lines status)
			*/
			int statusCTS = 0;
			int statusDSR = 0;
			int statusRING = 0;
			int statusRLSD = 0;
			bool successGetCommModemStatus = false;
			if (executeGetCommModemStatus) {
				DWORD lpModemStat;
				if (GetCommModemStatus(hComm, &lpModemStat)) {
					successGetCommModemStatus = true;
					if ((MS_CTS_ON & lpModemStat) == MS_CTS_ON) {
						statusCTS = 1;
					}
					if ((MS_DSR_ON & lpModemStat) == MS_DSR_ON) {
						statusDSR = 1;
					}
					if ((MS_RING_ON & lpModemStat) == MS_RING_ON) {
						statusRING = 1;
					}
					if ((MS_RLSD_ON & lpModemStat) == MS_RLSD_ON) {
						statusRLSD = 1;
					}
				}
				else {
					int lastError = (int)GetLastError();
					statusCTS = lastError;
					statusDSR = lastError;
					statusRING = lastError;
					statusRLSD = lastError;
				}
			}
			/*
			* Execute ClearCommError function if it's needed (get count of bytes in buffers and errors)
			*/
			int bytesCountIn = 0;
			int bytesCountOut = 0;
			int communicationsErrors = 0;
			bool successClearCommError = false;
			if (executeClearCommError) {
				DWORD lpErrors;
				COMSTAT *comstat = new COMSTAT();
				if (ClearCommError(hComm, &lpErrors, comstat)) {
					successClearCommError = true;
					bytesCountIn = (int)comstat->cbInQue;
					bytesCountOut = (int)comstat->cbOutQue;
					communicationsErrors = (int)lpErrors;
				}
				else {
					int lastError = (int)GetLastError();
					bytesCountIn = lastError;
					bytesCountOut = lastError;
					communicationsErrors = lastError;
				}
				delete comstat;
			}
			/*
			* Create int[][] for events values
			*/
			//returnArray = env->NewObjectArray(eventsCount, intClass, NULL);
			/*
			* Set events values
			*/
			for (int i = 0; i < eventsCount; i++) {
				switch (events[i]) {
				case EV_BREAK:
					returnValues[0] = (int)events[i];
					returnValues[1] = 0;
					goto forEnd;
				case EV_CTS:
					returnValues[1] = statusCTS;
					goto modemStatus;
				case EV_DSR:
					returnValues[1] = statusDSR;
					goto modemStatus;
				case EV_ERR:
					returnValues[1] = communicationsErrors;
					goto bytesAndErrors;
				case EV_RING:
					returnValues[1] = statusRING;
					goto modemStatus;
				case EV_RLSD:
					returnValues[1] = statusRLSD;
					goto modemStatus;
				case EV_RXCHAR:
					returnValues[1] = bytesCountIn;
					goto bytesAndErrors;
				case EV_RXFLAG:
					returnValues[1] = bytesCountIn;
					goto bytesAndErrors;
				case EV_TXEMPTY:
					returnValues[1] = bytesCountOut;
					goto bytesAndErrors;
				default:
					returnValues[0] = (int)events[i];
					returnValues[1] = 0;
					goto forEnd;
				};
			modemStatus: {
				if (successGetCommModemStatus) {
					returnValues[0] = (int)events[i];
				}
				else {
					returnValues[0] = -1;
				}
				goto forEnd;
			}
					 bytesAndErrors: {
						 if (successClearCommError) {
							 returnValues[0] = (int)events[i];
						 }
						 else {
							 returnValues[0] = -1;
						 }
						 goto forEnd;
					 }
								 forEnd: {
									 ;
								 };
			}
		}
		else {

			returnValues[0] = -1;
			returnValues[1] = (int)GetLastError();
		};
		CloseHandle(overlapped->hEvent);
		delete overlapped;
		return returnValues;
	}

	/*
	* Read data from port
	* portHandle - port handle
	* byteCount - count of bytes for reading
	*/
	vector<byte> SerialLib::readBytes(HANDLE portHandle, int byteCount) {
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

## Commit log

2017-09-30 Added HW and SW folders
    [BOM_ACTIVE_ELECTRODE.csv, BOM_CONVERSION_BOARD.csv, BOM_DAUGHTER_BOARD.csv, c2_creaminosimulinkmodel.obj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]
2017-10-08 Added Instructions.md to Arduino and Java interface
    [BOM_ACTIVE_ELECTRODE.csv, BOM_CONVERSION_BOARD.csv, BOM_DAUGHTER_BOARD.csv, c2_creaminosimulinkmodel.obj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]
2017-10-08 Simulink interface
    [c2_creaminosimulinkmodel.obj, c2_untitled.obj, creaminosimulinkmodel_sfun.obj, creaminosimulinkmodel_sfun_registry.obj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]
2017-10-08 Sketch Arduino
2017-10-08 Arduino libraries
2018-02-04 Added Calibration File
2018-02-04 Added Calibration.csv
    [Calibration.csv]
2018-02-28 Added Calibration
2018-02-28 Added Calibration to Simulink
    [Calibration.csv]
2018-03-07 Added Calibration.csv to BCI2000
    [Calibration.csv]
2018-03-10 Added Calibration.csv to OpenVIBe
2019-02-24 Gerber Files converted in RS-274X Format
    [cam.drl, pcb1.gbl, pcb1.gbo, pcb1.gbp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]
2019-02-25 Modified Gerber files
    [Layer_3.drl, Layer_8.drl, pcb2_assembly.gko]

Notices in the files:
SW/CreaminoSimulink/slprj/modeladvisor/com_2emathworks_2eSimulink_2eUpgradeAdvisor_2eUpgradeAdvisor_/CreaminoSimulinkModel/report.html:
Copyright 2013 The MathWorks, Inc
